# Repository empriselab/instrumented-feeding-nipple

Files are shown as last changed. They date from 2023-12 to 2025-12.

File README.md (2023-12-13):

# Instrumented Feeding Nipple

## CAD Files
All CAD files were printed using 5% rectilinear infill and no supports. A tutorial on how to construct the nipple can be found here: https://www.youtube.com/watch?v=TO4Haf6ZgnU

## Calibration 
The following must be run within `feeding_nipple_ws` which is the workspace to run the ATI Net F/T sensor.

### Step 1: Upload the Arduino code
Upload the `FeedingNippleArduino.ino` to your Arduino. Calibrate the upper and lower bounds of the analogRead and its corresponding voltages to ensure accurate readings. Be sure the readings are printing properly on the serial monitor. Ensure the serial monitor is closed throughout the duration of data collection.

### Step 2: Start ATI NET F/T sensor
Turn on the ATI NET F/T sensor. Open your terminal. Remember to run `source devel/setup.bash` everytime you open a new window in the root of your workspace to source it.

To initialize the core, type `roscore`.

In a new window, launch the sensor topic by typing `roslaunch netft_rdt_driver ft_sensor.launch ip_address:=192.168.1.6 bias:=True rate:=1000`.

To ensure the topic has been properly launched, type the command `rostopic echo /ft_sensor/netft_data`. This will allow you to monitor the readings from the F/T sensor in real time.

Calibrate the F/T sensor by holding it in the air and typing the command `rosservice call /ft_sensor/bias_cmd "cmd: 'bias'"`.

### Step 3: Begin collecting data
Run the bash script `callibration.sh` in the feeding_nipple_ws to begin collecting data from the ATI NET F/T sensor.

### Step 4: Convert Rosbag into CSV file
Place the `extract_forque.py` script in the same folder as your rosbag files. Run the `extract_forque.py` script. This converts the rosbag into a CSV in its own individual folder.

### Step 5: Combine the Force and Voltage Readings using CurveFit.py
Run this script with two CSVs files as the input - the voltage readings from the Arduino and the rosbag force readings. This script will combine the two csv files and calculate a calibration function in the form y = ae^(bx).

## Post-Calibration 
After finding the calibration function, input the a and b parameters into `TranslateV2F.py`. Whenever performing future tests or in field tests, have `FeedingNippleArduino.ino` running on the Arduino before running `TranslateV2F.py`.

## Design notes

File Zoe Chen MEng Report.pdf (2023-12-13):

# DESCRIBING CHANGES IN SUCKLE BEHAVIOR VIA TACTILE FEEDING NIPPLE BETWEEN HEALTHY & SICK DAIRY BREED CALVES

A Design Project Report

Presented to the School of Electrical and Computer Engineering of Cornell University

in Partial Fulfillment of the Requirements for the Degree of

Master of Engineering, Electrical and Computer Engineering

Submitted by

Zoe Mallorie Chen

MEng Field Advisor: Tapomayukh Bhattacharjee

MEng Outside Advisor: Taika von Königslöw

Degree Date: January 2024

INSTRUMENTED CALF FEEDING NIPPLE

# Abstract

Master of Engineering Program

School of Electrical and Computer Engineering

Cornell University

Design Project Report

Project Title:
Describing Changes in Suckle Behavior Via Tactile Feeding Nipple Between Healthy & Sick Dairy Breed Calves

Author:
Zoe Mallorie Chen

Abstract:
Treating young calves promptly is challenging for caregivers because the diagnosis process is labor intensive and potentially a biohazard when multiple calves are involved. Previous studies have found that sickly calves exhibit weak suckling behavior – however, exact quantifiable differences in the bite force have yet to be defined. The goal is to create a robust instrumented feeding nipple that characterizes suckling behavior in the two groups. In the current iteration, we created a system that accurately measures bite forces of up to 50N and conducted preliminary field tests using portable milk feeders. We hope to integrate it into the commercial automated milk feeders to provide a quantified indicator of illness for early treatment and to improve clinical outcomes.

1

## 1 Executive Summary

Weaker biting forces correlate to diseased calves, especially those under six months suffering from diarrhea. The planned final product is a sensor that fits within current calf feeding systems to record the bite force of calves during the suckling process – in hopes of providing another illness indicator that is safer and more convenient for caregivers. The product must be rugged enough to withstand variations in temperature, exposure to liquids, and over fourteen thousand bites over its lifetime – all while maintaining a soft exterior that is comfortable for the calves to chew on.

The current iteration of the sensor is modeled after the feeding nipples attached to portable calf milk feeding bottles. Two force resistive sensors (FSRs) are encapsulated within two silicon layers and wired to a Wheatstone bridge. The output voltage is converted to a force via a calibration function in the form of an exponential growth function. All voltage-to-force translations are done on an Arduino Nano 33 IOT in real-time. The total cost of the sensor is $20.36, excluding the cost of the microcontroller.

We have validated that the design’s calibration function adequately fits the industry standard. Comparisons between the developed sensor and the ground truth force have shown that the sensor accurately and precisely measures the true force up to 50N, with an error of ±3.09N.

Preliminary field testing found that healthy bites (N=160) had an average force of 14.97N with a standard deviation of 4.30N, while weak bites (N=221) had an average force of 4.55N with a standard deviation of 2.35N.

2

## 2 Background

To assess a calf’s condition during health checks, caregivers typically look for subtle visual cues (e.g. depression, alertness) [3]. Reliance on these cues remains an issue because cows are a prey species and tend to hide their sickness as a protection mechanism against predators. Once signs of sickness present themselves, such as diarrhea and dehydration, the calf may have already sustained damage to its internal organs – driving the need for systems that help caregivers predict or detect illness in calves earlier than currently possible [3].

A few quantitative measures exist to help with the earlier identification of sick calves, such as elevated rectal temperatures. However, these methods provide no continuous monitoring options, are time-consuming, or require direct contact with feces– which may become a biohazard because of zoonotic pathogens [5].

Previous studies have shown that sickly calves generally have weaker suckling behavior than their healthy counterparts, but quantifiable differences in the bite forces between these two groups have yet to be defined [3]. The goal of this project is to create a sensor that defines the bite force differences between healthy and sickly calves, with the hopes of developing a general tactile sensor fit for rugged conditions.

3

## 3 Design Requirements

The sensor developed for this project must be embedded within feeding nipples used on portable milk feeding bottles. These feeding nipples are typically replaced once every 2 weeks, subjected to a wide range of temperatures, and exposed to liquids.

Given these standards, we aim to embed a sensor that measures bite force within a feeding nipple, ensuring that the final product is capable of:

- Accurately and precisely measuring bite forces of up to 50N
- Withstanding over fourteen-thousand chews without signal degradation
- Working when external liquids are introduced
- Maintaining consistent signal readings during temperature fluctuations
- Being inexpensive to facilitate frequent replacements

4

## 4 Implementation

### 4.1 Force Sensors

Force sensing resistors (FSRs) were chosen for this iteration among capacitance and magnetic sensors because of their durability, circuit simplicity, noise resistance, force repeatability, and lost cost of production. These sensors must also be flexible enough for the calves to chew on and must be able to differentiate between forces of at least up to 11N, as estimated by our calculation from the typical bite pressure and surface area of a calf’s molars:

236 kPa × 0. 0075 m × 0. 006 m = 10. 62N

Given these requirements, we chose the Interlink Electronics FSR UX 406 series. Both long and short versions of this FSR were tested. Although the long version had more structural integrity, the final design opted for the short version because of our size constraints [2].

### 4.2 Mechanical Assembly

### 4.2.1 Silicon Mixture

Various mixtures of silicon were tested to create a product most similar in texture and stiffness to the current silicon rubber nipples on portable milk feeding containers. The final product utilizes Smooth-On PMC™-770, a mixture that has a shore hardness of 70A or similar to the sole of a shoe.

Thirty grams of Part A and fifteen grams of Part B of PMC™-770 are thoroughly mixed before being poured into 3 custom 3D printed molds. The result from the custom molds are as follows:

- A cylindrical inner layer that protects the sensors from milk within the feeder.
- A cylindrical outer layer that protects the sensor from degradation from the environment and calf chewing.
- A circular ring adhered to the outer and inner layer to keep the nipple attached to the bottle.

5

All molds are left to cure for at least sixteen hours at room temperature before being demolded.

### 4.2.2 FSR Wire Extensions

To date, the FSR UX 406 from Interlink Electronics only offers solder tab connections. Two wires are soldered onto those tabs – with careful consideration towards the heat of the soldering iron and stress applied to the joint, as these tabs are very fragile. We have found that wrapping the joint in electrical tape and setting the temperature of iron to just enough for the solder to melt significantly reduces the chance of tab breakages.

### 4.2.3 Components Layering

Two types of glue are used to ensure the FSRs stay in their designated areas during the setting and drying process. RapidFuse® All-Purpose Adhesive has a quick set time of thirty seconds and is initially applied to ensure the FSRs are centered throughout the entire glue curing process. E6000, an industrial strength adhesive, is then applied to increase the bond strength between the FSRs and the silicon rubber.

Four FSRs, two on each hemisphere, are adhered to the cylindrical inner layer by applying small amounts of RapidFuse® All-Purpose Adhesive to the back of the FSRs. The FSRs are held in place until the glue sets before E6000 is then applied to the back of the FSRs. A custom 3D print has been created to hold the FSRs in a circular shape during the curing process. After the E6000 is cured, the FSRs and the inner cylindrical layer is encapsulated within the outer cylindrical layer and the two layers are adhered to the silicon circular ring using the E6000. The wires from the FSRs are routed through the ring or above the ring depending on whether a milk or no milk version of the nipple is being created.

For the milk version of the nipple, a custom 3D printed box with a lid has been created to house the circuitry. The box is attached to the box via velcro. If opting for a no milk version of the nipple, a panel the size of the breadboard is cut out of the milk container and attached back to the container using a plastic hinge to create a panel for easy access to the circuitry. The breadboard can be attached to the panel via velcro or other adhesives.

6

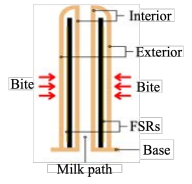
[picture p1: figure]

Figure 1. Cross section of a feeding nipple with only two FSRs.

Figure 2. Non-milk version of the manufacturing sample, with circuitry attached to a panel created by cutting out the portable milk feeder.

7

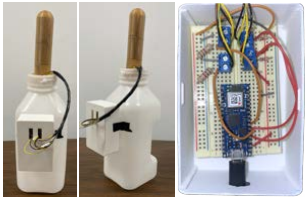
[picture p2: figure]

Figure 3. Milk version of the manufacturing sample, with circuitry (left) attached to the side of the portable feeder (right, middle).

### 4.3 Circuitry

The original circuitry design featured four FSRs, each a part of a two resistor voltage divider circuit. Initially testing found that this circuitry provided a narrow voltage output range of 0 to 2000 mV to forces between 0 to 50N – making it difficult to map a voltage to a force with certainty.

The final circuitry design instead features a pair of FSRs connected in one wheatstone bridge – for a total of two wheatstone bridges in this iteration of the project. Pairs of the wheatstone bridge are defined as FSRs that are directly across from each other on the nipple. To determine the values of R2 and R3, the following equation was used:

Vout = Vdd( | ,

R3
R

FSR1+R3 − R FSR2 R2 + R FSR2 )

such that the output voltage is 0 when no force is applied. The working principle is that when a calf bites on the FSRs, the resistances of those FSRs simultaneously decreases, causing the positive and negative terminals of the output voltage to increase and decrease respectively. This resulted in a new output voltage range of -3300mV to 1000mV, doubling the voltage range that we can map onto a bite force.

8

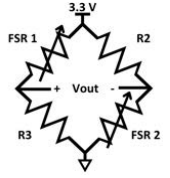
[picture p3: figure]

Figure 4. Schematic for one wheatstone bridge configuration.

### 4.4 Calibration

A drill press vise with a stationary base and the ATI Net F/T sensor were used to map the output voltages from the wheatstone bridge to a bite force. The Net F/T sensor is an external device we used to define the industry standards for force measuring instruments – which will now be referred to as the ground-truth force. The manufactured product and the Net F/T sensor were placed between the stationary and moving jaw.

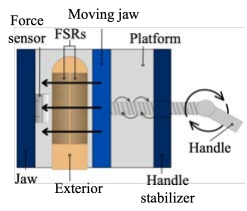
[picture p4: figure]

Figure 5. Sketch of the calibration setup using a bench drill press vise and ATI Net F/T sensor.

9

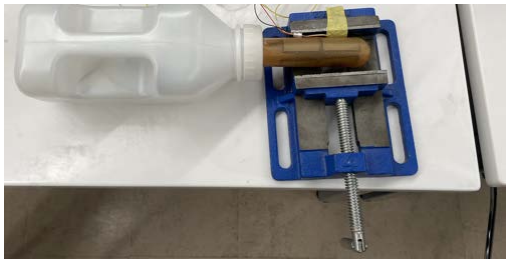
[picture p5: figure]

Figure 6. Manufactured sample placed inside drill press with force sensor, which is attached using yellow tape.

Thirty thousand samples from both the Net F/T sensor and the output voltage were recorded before being averaged by ground-truth force. The trend between increases in the output voltage and the ground-truth force most closely followed an exponential growth form with a standard deviation of ±3.09N, which was used as the mathematical model to relate the ground-truth force and the output voltage.

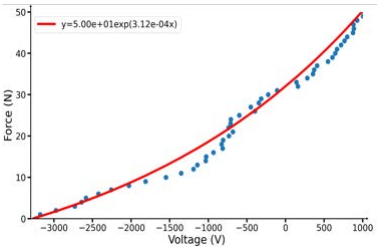
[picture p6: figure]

Figure 7. Voltage-force relation when force is applied. Line of best fit is shown in red for one specific sample.

10

## 5 Validation

Comparisons between the force estimates from the proposed product and the ground-truth force were conducted, using the drill press vise to mimic a chewing motion. Our trials found that our sensor’s estimates were within one standard deviation of the ground-truth force sensors from 0 to 50 N.

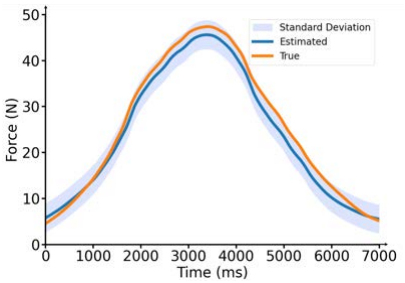
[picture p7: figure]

Figure 8. Estimated force (dark blue) with standard deviation (light blue) and ground truth force from external sensor (orange).

Trials were also conducted with live calves to determine whether the proposed product was capable of sensing differences between weak and healthy bite forces during suckling behaviors. During these experiments, weak bites were defined as non-suckling chewing behavior, such as play. Our trials found that healthy bites (N=160) had an average force of 14.97N with a standard deviation of 4.30N, while weak bites (N=221) had an average force of 4.55N with a standard deviation of 2.35N. The FSRs during these trials showed no signs of signal degradation and no major deformations were found on the silicon nipples after chewing.

11

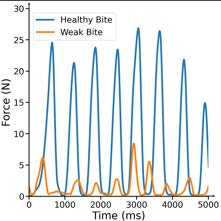
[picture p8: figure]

Figure 9. Estimated force from calves with healthy and weak bites.

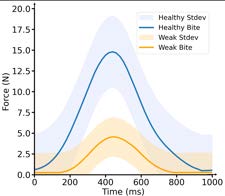
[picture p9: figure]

Figure 10. Average healthy (N = 160) and weak (N = 221) bites force from field trials.

12

## 6 Conclusion

Our testing and preliminary tests revealed some flaws with the current iteration of the proposed product. The current iteration with four FSRs total has a diameter and length that is too wide to comfortably fit within the mouth of calves – which caused the calves to engage in play behavior instead of suckling behavior. A smaller and narrower sensor with only two FSRs total should be developed to consistently encourage calf suckling behavior.
In addition, the generalized mathematical function | typically y = ae

bx
does not translate well from sample to sample due to inconsistencies in the manufacturing process, and thus requires the parameters and to be calibrated a b for each specific sensor.
This iteration of the sensor requires a microcontroller with a wired connection to communicate with the serial monitor and allow a Python program to write the data into a csv file. Future iterations of this sensor should be self contained to make the sensor truly portable and for caregiver ease.
Finally, the total cost of the sensor is $20.36, excluding the cost of the Arduino 33 IOT. Considering that typical cow feeding nipples range from $1 to $4 and that these nipples are replaced frequently, a less expensive sensor should be developed. The largest factor in our sensor cost were the four FSRs, which totaled $19.96. Even if a sensor were developed with only two FSRs to more comfortably fit within the calf’s mouth, the total cost would still exceed our requirements. One possible solution is to create flex sensors ourselves, which are considerably cheaper than those on the market [1][4]. Further testing is required to characterize these homemade flex sensors and how they compare to commercially available FSRs.

13

## 7 Appendix

A video tutorial of the process described below can be found here. (https://youtu.be/TO4Haf6ZgnU)

### 7.1 Nipple Construction

### 7.1.1 Silicon Molding

The custom molds are 3D printed with a 5% infill and PLA. A version of the molds for two FSRs have been provided. Line your surface with aluminum foil. Measure 15g and 7.5g of Part A and Part B of Smooth-On PMC™-770 using a scale and pour the mixture into a disposable cup. Mix together thoroughly for 3 minutes using a wooden tongue depressor. Spray a thin coating of Universal™ Mold Release, or any mold release, onto all surfaces of the outer layer, inner layer, and ring molds. Make sure the coat is evenly distributed using a paint brush. Pour your silicon mixture into the base molds and place the shapers in their respective base molds. The shapers should snap into place using the prongs from the base molds. Allow to cure for at least 16 hours before demolding.

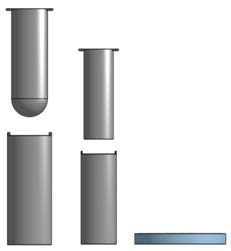
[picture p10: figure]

Figure 11. CAD models for the custom molds of the nipple for only two FSRs. Bottom: the base mold for the outer layer (left), the inner layer (middle), and the

14 ring. Top: the shaper of the outer mold (left) and the shaper for the inner mold (middle).

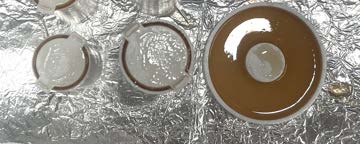
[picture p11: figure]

Figure 12. Top view of the inner layer (left), outer layer (middle), and ring (right) molds with silicone poured into them.

Figure 13. Side view of all molds, closeup of the outer layer mold (middle), and closeup of the ring mold (right).

Sometimes, the silicon expands, making it difficult to remove from the mold by sliding the shaper out. In this case, use the backside of a hammer to break a line down the center of molds.

15

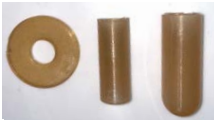
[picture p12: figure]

Figure 14. Silicon parts demolded.

### 7.1.2 FSR Wire Extensions

Solder two 24 AWG wires onto each lead of each FSRs. Be sure to heat the soldering iron to the minimum temperature required to melt the solder, as excessive heat may damage the leads of the FSR and cause them to melt off. To minimize breakage at these points, wrap the leads with tape.

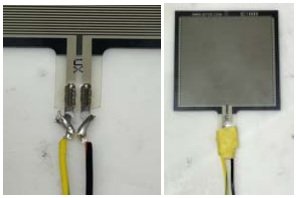
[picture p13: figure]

Figure 15. FSR soldered with 24 AWG wires (left) and wrapped with tape (right).

### 7.1.3 Component Layering

Once all the FSRs are soldered, apply a small amount of RapidFuse® All-Purpose Adhesive to the back of the FSRs and adhere them to the silicon inner layer. Place inside the custom 3D printed holder and wait for 30 minutes, or until the glue cures. Once that glue cures, add E6000 adhesive to the back of the FSRs. Allow to cure for 24 hours.

16

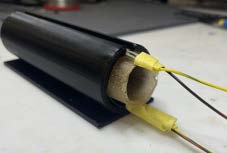
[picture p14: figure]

Figure 16. FSRs glue and placed into a custom 3D printed holder.

After the E6000 cures, encapsulate the inner layer with the outer layer and glue both to the ring using the E6000. Place upright and allow to dry for 24 hours. This nipple should screw onto the portable milk feeder.

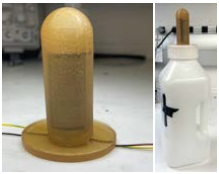
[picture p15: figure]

Figure 17. Constructed nipple (left) and screwed into feeder (right).

### 7.2 Calibration

Place the sensor within the two jaws of a drill press vise with a stationary base. Attach the ATI Net F/T sensor to the stationary jaw of the drill press vise such that it directly aligns with the center of one of the FSRs (Figure 6). When calibrating, be sure that voltage outputs from all forces ranging from 0 to 50N, in increments of 5N or less, are being recorded. Code to start the FT sensor, the Arduino, and to combine the readings between the two devices to generate a mathematical model.

17

## References

[1] Ardi Wiranata et al., “A DIY Fabrication Approach of Stretchable Sensors Using Carbon Nano Tube Powder for Wearable Device,” Frontiers in Robotics and AI, vol. 8, Nov. 2021, doi: https://doi.org/10.3389/frobt.2021.773056.
[2] “FSR UX 406 Short,” Interlink Electronics Shop. https://buyinterlinkelectronics.com/products/fsr-ux-406-short
[3] G. L. Lowe, M. A. Sutherland, J. R. Waas, A. L. Schaefer, N. R. Cox, and M. Stewart, “Physiological and behavioral responses as indicators for early disease detection in dairy calves,” Journal of Dairy Science, vol. 102, no. 6, pp. 5389–5402, Jun. 2019, doi: https://doi.org/10.3168/jds.2018-15701.
[4] K. Elgeneidy, G. Neumann, M. Jackson, and N. Lohse, “Directly Printable Flexible Strain Sensors for Bending and Contact Feedback of Soft Actuators,” Frontiers in Robotics and AI, vol. 5, Feb. 2018, doi: https://doi.org/10.3389/frobt.2018.00002.
[5] Mikolt Bakony, Levente Kovács, Luca Fruzsina Kézér, and V. Jurkovich, “The use of body surface temperatures in assessing thermal status of hutch-reared dairy calves in shaded and unshaded conditions,” Frontiers in Veterinary Science, vol. 10, Jul. 2023, doi: https://doi.org/10.3389/fvets.2023.1162708.

18

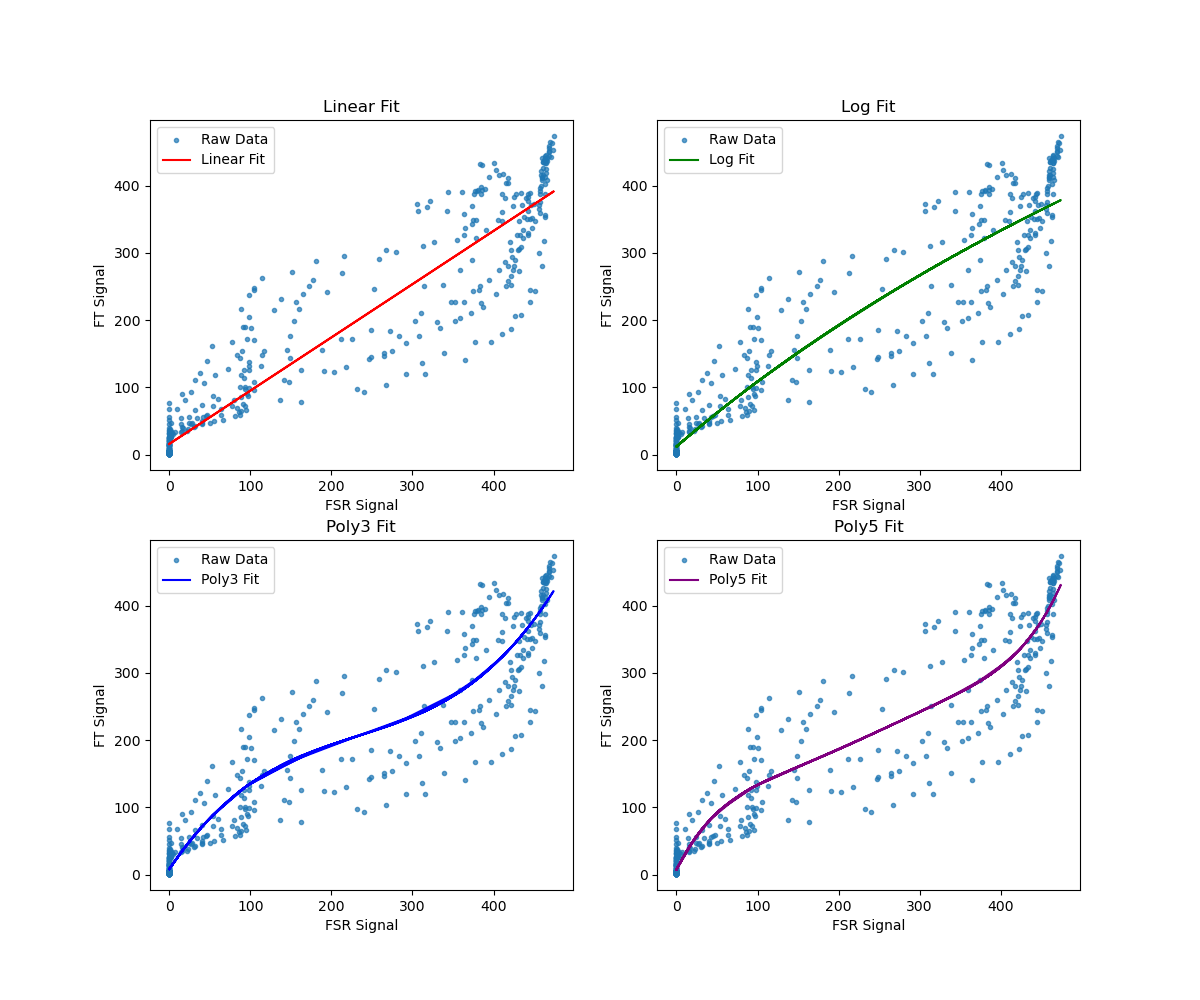
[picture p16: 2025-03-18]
scripts/diff_fit_models.png

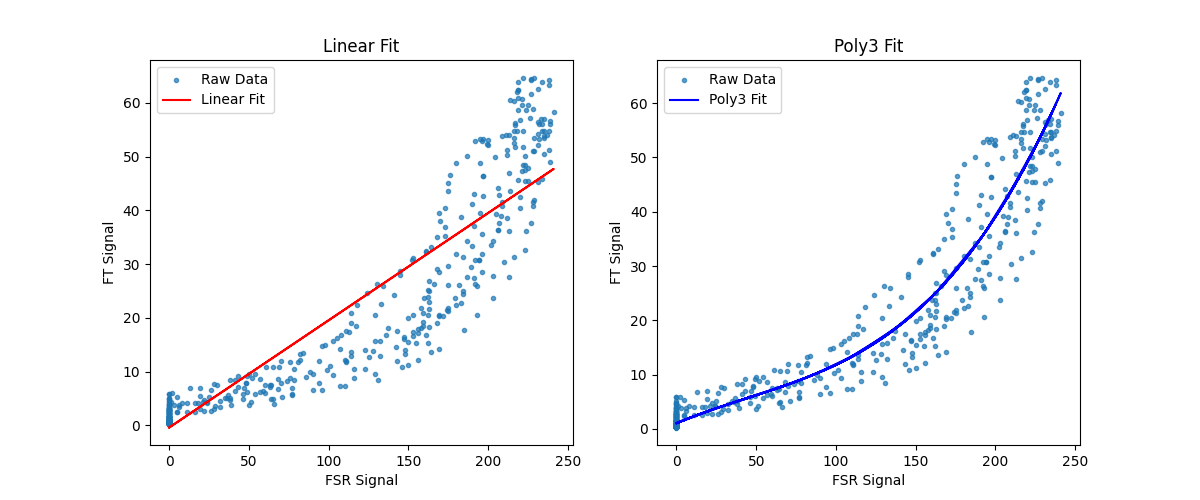
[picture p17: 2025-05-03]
scripts/flat_iter_1_diff_fit_models.png

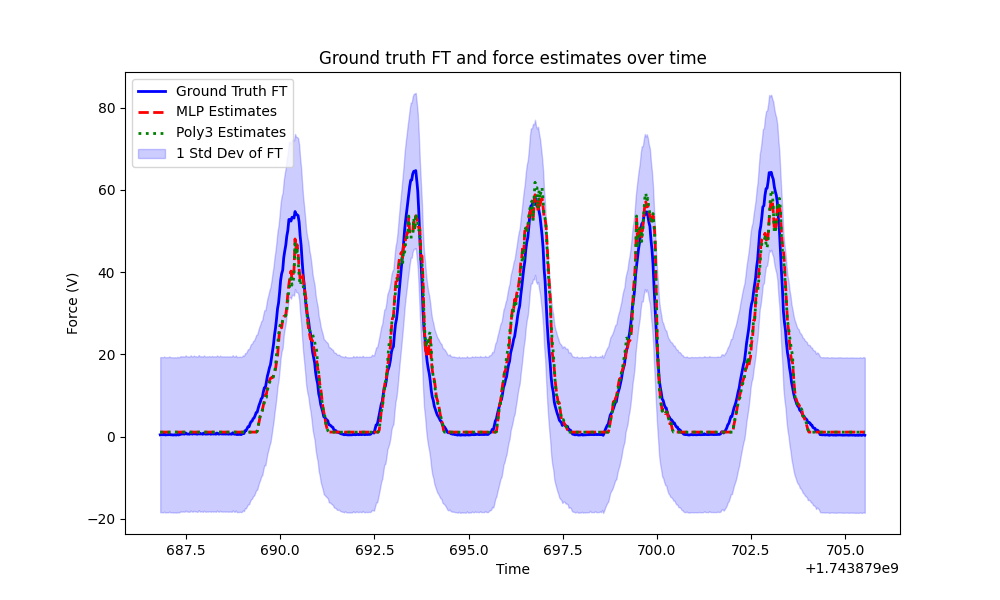
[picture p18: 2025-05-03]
scripts/flat_iter_1_compare_time_force.png

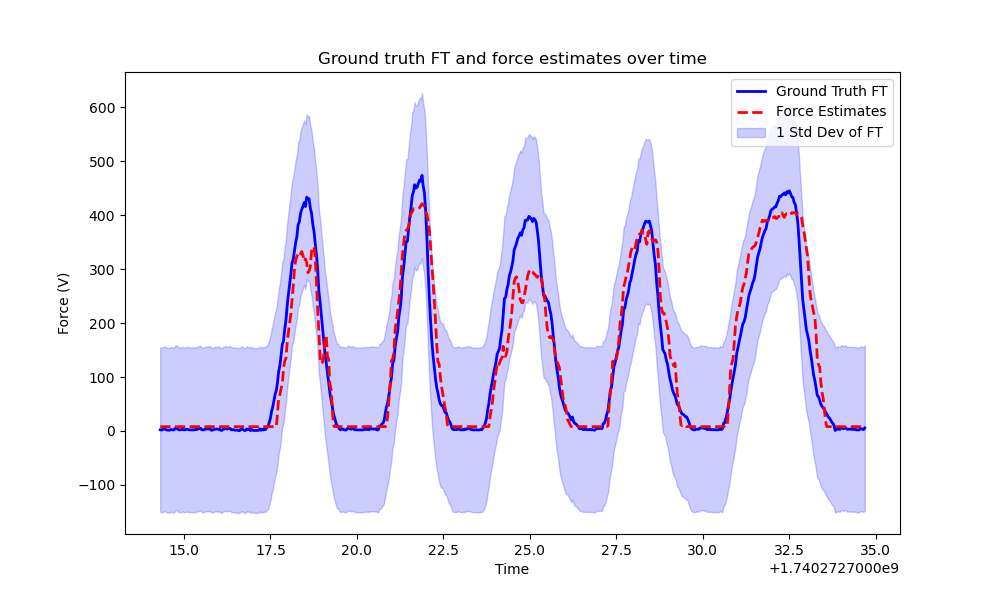
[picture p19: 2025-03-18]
scripts/compare_time_force.png

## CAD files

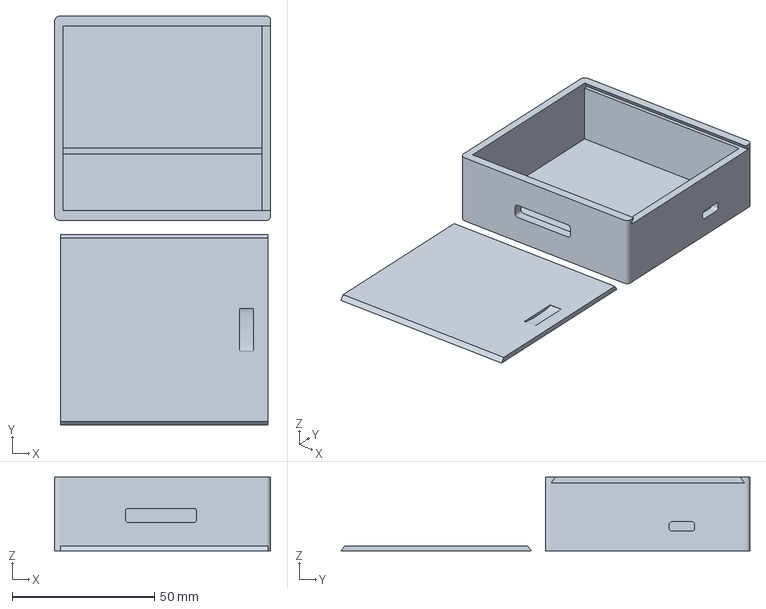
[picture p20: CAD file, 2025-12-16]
CAD/Instrumented Feeding Bottle Box v2.3mf
76.0 x 143.8 x 26.0 mm

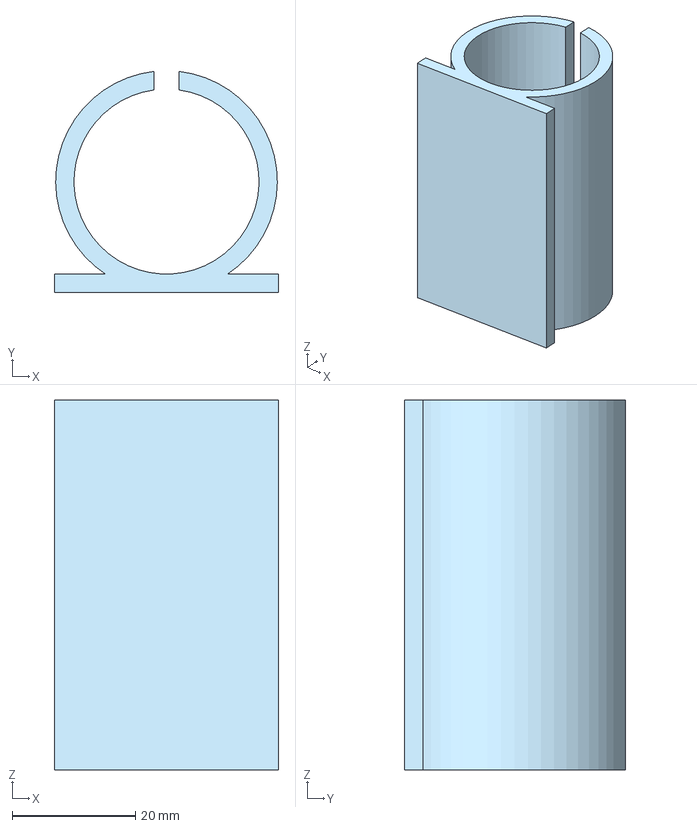
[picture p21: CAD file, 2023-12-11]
CAD/DryingRack.step
36.3 x 35.9 x 60.0 mm

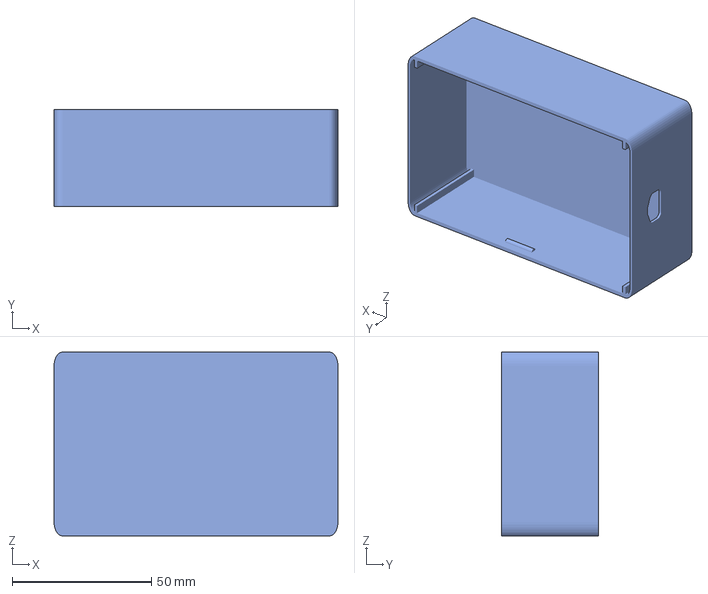
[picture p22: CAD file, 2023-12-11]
CAD/BreadboardBoxCase.step
102.0 x 35.0 x 66.0 mm

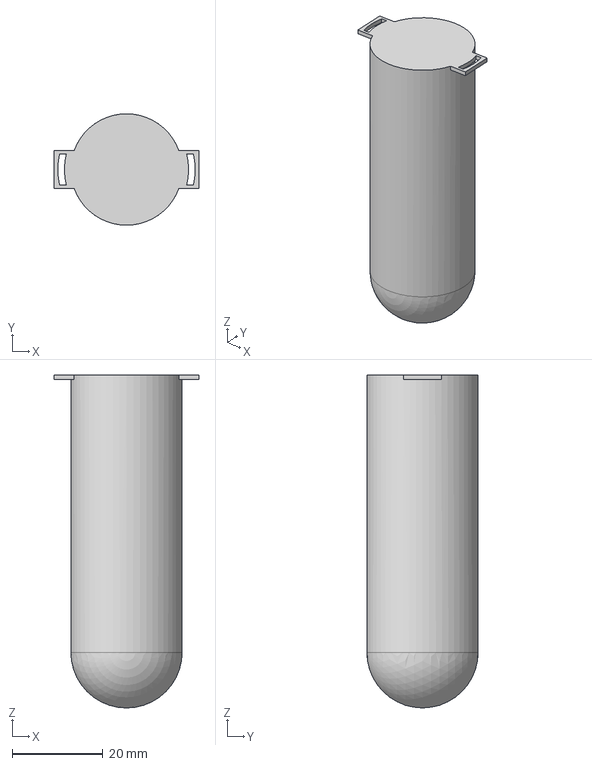
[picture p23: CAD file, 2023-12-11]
CAD/Outer Mold - Shaper.step
31.8 x 24.5 x 73.2 mm

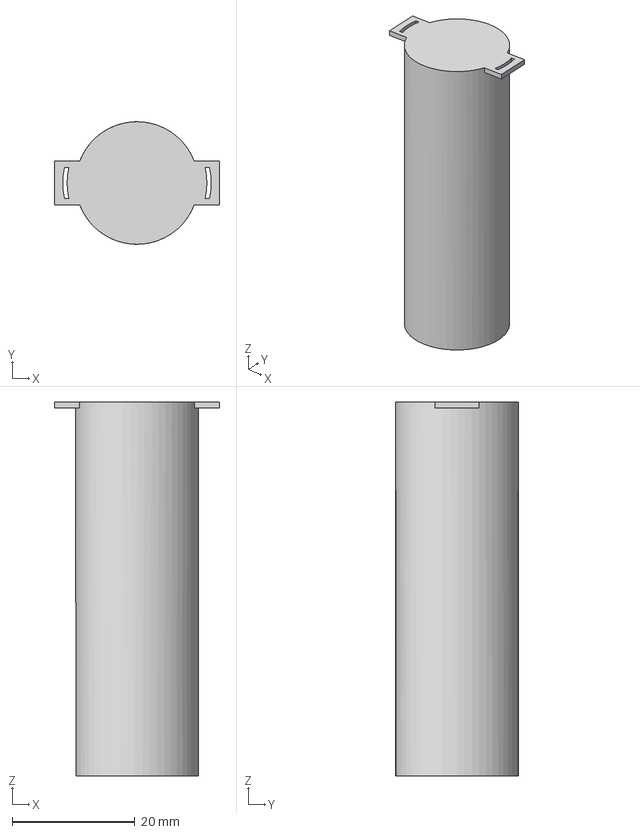
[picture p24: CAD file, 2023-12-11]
CAD/Inner Mold - Shaper.step
26.9 x 20.0 x 61.0 mm

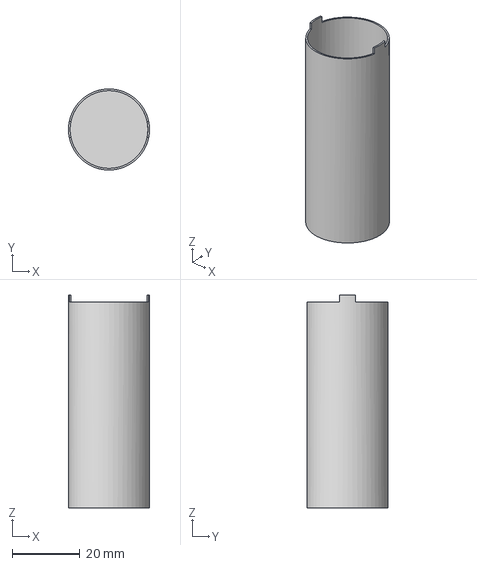
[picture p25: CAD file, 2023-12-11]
CAD/Inner Mold - Outer Container.step
24.0 x 24.0 x 63.0 mm

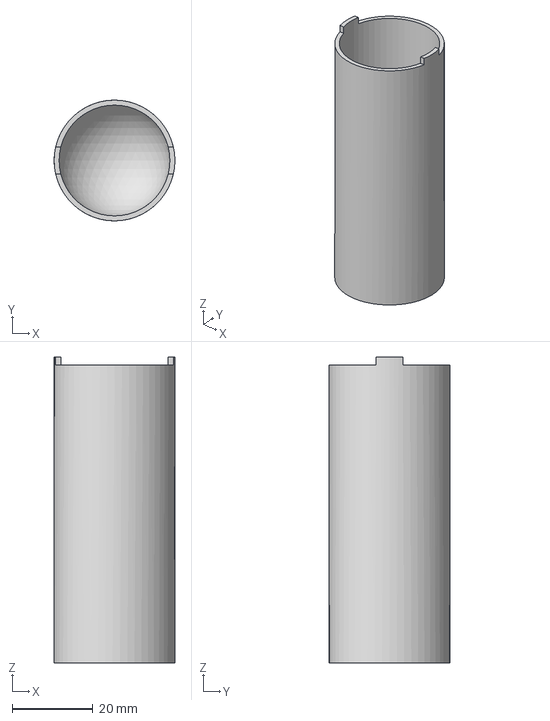
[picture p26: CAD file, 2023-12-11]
CAD/Outer Mold - Container.step
30.0 x 30.0 x 76.0 mm

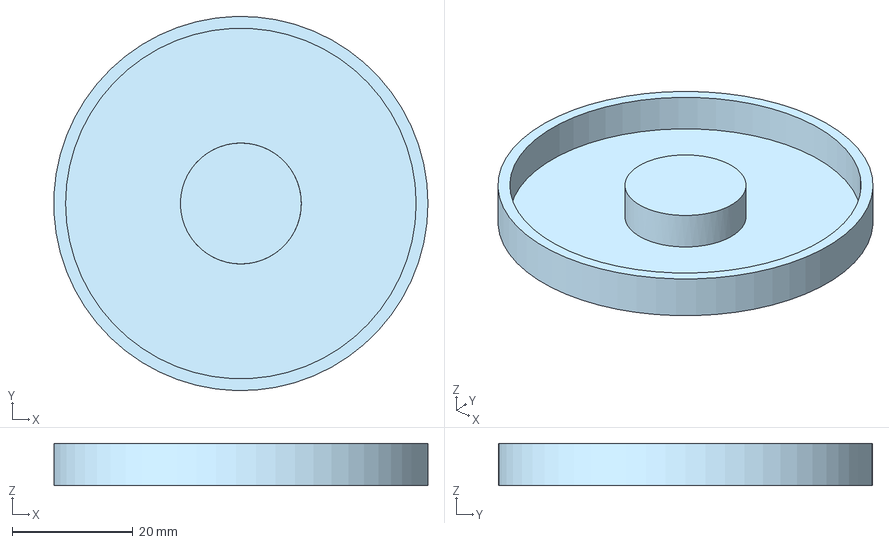
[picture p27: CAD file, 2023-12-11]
CAD/Ring.step
61.9 x 61.9 x 7.00 mm

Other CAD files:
CAD/BreadboardBoxLid.step

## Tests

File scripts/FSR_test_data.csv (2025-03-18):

Timestamp | FSR 1 (mV) | FSR 2 (mV) | FSR 3 (mV) | FSR 4 (mV) | FSR 5 (mV) | FSR 6 (mV) | FSR 7 (mV) | FSR 8 (mV)
1740272712.2905614 | 4 | 662 | 491 | 767 | 453 | 625 | 660 | 823
1740272712.3242462 | 12 | 597 | 482 | 768 | 453 | 626 | 659 | 822
1740272712.3612447 | 10 | 596 | 482 | 768 | 453 | 626 | 659 | 821
1740272712.393989 | 11 | 599 | 483 | 769 | 453 | 626 | 659 | 820
1740272712.4268672 | 10 | 599 | 482 | 768 | 453 | 626 | 659 | 820
1740272712.4635546 | 11 | 597 | 481 | 768 | 453 | 626 | 659 | 820
1740272712.4957674 | 11 | 598 | 482 | 768 | 453 | 625 | 659 | 820
1740272712.5285187 | 11 | 599 | 482 | 768 | 453 | 626 | 659 | 820
1740272712.5651255 | 10 | 597 | 482 | 768 | 454 | 625 | 659 | 820
1740272712.5985641 | 10 | 597 | 482 | 768 | 453 | 626 | 659 | 820
1740272712.6349564 | 11 | 598 | 482 | 768 | 453 | 625 | 659 | 820
1740272712.6677067 | 11 | 599 | 481 | 765 | 454 | 624 | 659 | 820
1740272712.7013493 | 11 | 598 | 483 | 768 | 453 | 626 | 659 | 820
1740272712.7376175 | 11 | 598 | 483 | 768 | 453 | 626 | 659 | 820
1740272712.7703927 | 11 | 599 | 482 | 768 | 453 | 625 | 659 | 820
1740272712.8035338 | 11 | 597 | 482 | 767 | 454 | 626 | 659 | 820
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

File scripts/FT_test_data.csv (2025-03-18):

ft_time | ft
1740272714.3016016 | -0.19743083302020992
1740272714.302462 | -0.17948224453826603
1740272714.3034663 | -0.20844243196550447
1740272714.3044705 | -0.2187319158313526
1740272714.3054733 | -0.17101106203861202
1740272714.3064775 | -0.217084160826473
1740272714.307481 | -0.5791213030014477
1740272714.3084843 | -0.38585826885157515
1740272714.3094873 | -0.44596411802688196
1740272714.3104913 | -0.17453741164178502
1740272714.3114953 | -0.19585322173713085
1740272714.3124988 | -0.2281481302720972
1740272714.3135018 | -0.37197490208788775
1740272714.3145046 | -0.32694662341858444
1740272714.315509 | -0.2478086346029407
1740272714.3165133 | -0.29067436110165173
1740272714.3175168 | -0.1737111814015836
1740272714.3185203 | -0.15331018309862463
1740272714.3195236 | -0.16424768230149844
1740272714.3205295 | -0.16442833284921973
1740272714.3215325 | -0.14062355664913956
1740272714.3225367 | -0.1457234366806307
1740272714.323545 | -0.1570450338300895
1740272714.324543 | -0.5178950170235416
1740272714.325546 | -0.3582621785311061
1740272714.3265502 | -0.18045592132832347
1740272714.3275535 | -0.1525393731159726
1740272714.3285575 | -0.1684101787797096
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

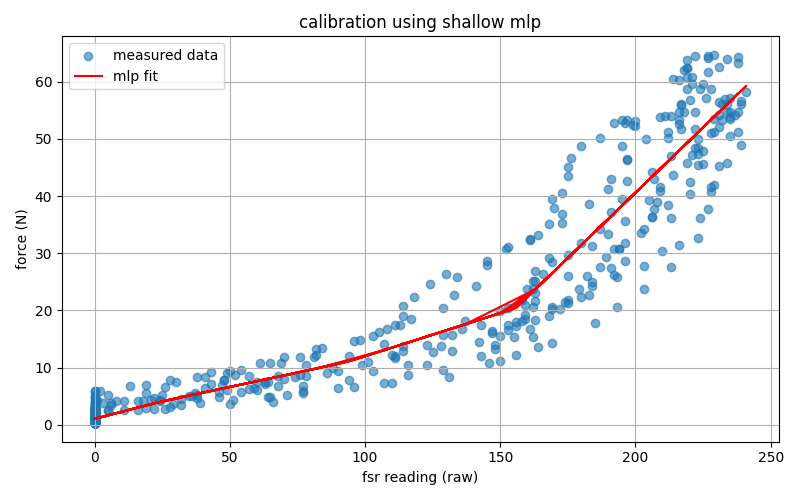
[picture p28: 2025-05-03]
scripts/flat_mlp_calibrated.png

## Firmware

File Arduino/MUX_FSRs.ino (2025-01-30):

// Pin declarations for the sensors and MUX control
int pos_Vout = A0; // Assume the multiplexer output is connected to A0
int neg_Vout = A1;
const int muxS0 = 2; // Multiplexer control pins
const int muxS1 = 3;
const int muxS2 = 4;
// const int muxS3 = 5;

// Number of FSRs and MUX channels
const int numFSRs = 16;

// Array to store offsets for zeroing out readings
float offset[numFSRs] = {0};

// Number of samples to collect for calibration and averaging
const int numSamples = 10;

void setup() {
  Serial.begin(9600);  // Initialize the serial communication

  // Set MUX control pins as output
  pinMode(muxS0, OUTPUT);
  pinMode(muxS1, OUTPUT);
  pinMode(muxS2, OUTPUT);
  pinMode(muxS3, OUTPUT);

  // Calibrate offsets
  Serial.println("Calibrating offsets...");
  calibrateOffsets();
  Serial.println("Calibration complete!");
}

void loop() {
  for (int fsrIndex = 0; fsrIndex < numFSRs; fsrIndex++) {
    // Set MUX to the correct channel for the current FSR
    setMuxChannel(fsrIndex);
    delay(5); // Allow time for MUX to settle

    // Initialize variables for averaging
    long sumForceReading = 0;

    // Read and sum samples
    for (int i = 0; i < numSamples; i++) {
      float sensorUpper = analogRead(pos_Vout);
      float sensorLower = analogRead(neg_Vout);
      sumForceReading += (sensorUpper - sensorLower);
    }

    // Calculate the average and apply offset
    float average = (float)sumForceReading / numSamples - offset[fsrIndex];

    // Print the reading for the current FSR
    Serial.print("FSR ");
    Serial.print(fsrIndex);
    Serial.print(": ");
    Serial.println(average);
  }

  delay(100); // Adjust delay as needed for reading frequency
}

// Function to calibrate offsets
void calibrateOffsets() {
  for (int fsrIndex = 0; fsrIndex < numFSRs; fsrIndex++) {
    // Set MUX to the correct channel for the current FSR
    setMuxChannel(fsrIndex);
    delay(5); // Allow time for MUX to settle

    // Initialize variables for averaging
    long sumForceReading = 0;

    // Read and sum samples
    for (int i = 0; i < numSamples; i++) {
      float sensorUpper = analogRead(pos_Vout);
      float sensorLower = analogRead(neg_Vout);
      sumForceReading += (sensorUpper - sensorLower);
    }

    // Calculate the average and store as offset
    offset[fsrIndex] = (float)sumForceReading / numSamples;

    Serial.print("Offset for FSR ");
    Serial.print(fsrIndex);
    Serial.print(": ");
    Serial.println(offset[fsrIndex]);
  }
}

// Function to set the MUX channel
void setMuxChannel(int channel) {
  digitalWrite(muxS0, channel & 0x01);
  digitalWrite(muxS1, (channel >> 1) & 0x01);
  digitalWrite(muxS2, (channel >> 2) & 0x01);
  digitalWrite(muxS3, (channel >> 3) & 0x01);
}

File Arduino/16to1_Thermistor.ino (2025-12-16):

#include <math.h>

// --- MUX FSR SETUP ---
const int muxSigPin = A0;       // MUX signal pin (connected to FSRs)
const int s0Pin = 2;            // MUX control pins
const int s1Pin = 3;
const int s2Pin = 4;
const int s3Pin = 5;

const int numFSRChannels = 12;  // Number of FSRs
int fsrReadings[numFSRChannels];

// --- Thermistor SETUP ---
#define THERMISTORPIN A1  
#define THERMISTORNOMINAL 10000      
#define TEMPERATURENOMINAL 25   
#define NUMSAMPLES 5
#define BCOEFFICIENT 3950
#define SERIESRESISTOR 10000    

int samples[NUMSAMPLES];

void setup() {
  Serial.begin(9600);

  // MUX control pins
  pinMode(s0Pin, OUTPUT);
  pinMode(s1Pin, OUTPUT);
  pinMode(s2Pin, OUTPUT);
  pinMode(s3Pin, OUTPUT);

  // Initialize MUX control lines
  digitalWrite(s0Pin, LOW);
  digitalWrite(s1Pin, LOW);
  digitalWrite(s2Pin, LOW);
  digitalWrite(s3Pin, LOW);

  analogReference(AR_EXTERNAL);
}

void loop() {
  // --- Read FSRs ---
  for (int channel = 0; channel < numFSRChannels; channel++) {
    selectMuxChannel(channel);
    fsrReadings[channel] = analogRead(muxSigPin);
  }

  // --- Read Thermistor ---
  float average = 0;
  for (int i = 0; i < NUMSAMPLES; i++) {
    samples[i] = analogRead(THERMISTORPIN);
    delay(2);
  }
  for (int i = 0; i < NUMSAMPLES; i++) {
    average += samples[i];
  }
  average /= NUMSAMPLES;

  // Convert ADC reading to resistance
  average = 1023.0 / average - 1.0;
  average = SERIESRESISTOR / average;

  float steinhart;
  steinhart = average / THERMISTORNOMINAL;
  steinhart = log(steinhart);
  steinhart /= BCOEFFICIENT;
  steinhart += 1.0 / (TEMPERATURENOMINAL + 273.15);
  steinhart = 1.0 / steinhart;
  steinhart -= 273.15;

  // --- Print Data in One Line: FSR1 FSR2 ... TempC ---
  for (int i = 0; i < numFSRChannels; i++) {
    Serial.print(fsrReadings[i]);
    Serial.print(" ");
  }
  Serial.println(steinhart);  // temperature in °C
}

// --- Select MUX Channel ---
void selectMuxChannel(int channel) {
  digitalWrite(s0Pin, (channel & 0x01));
  digitalWrite(s1Pin, (channel & 0x02) >> 1);
  digitalWrite(s2Pin, (channel & 0x04) >> 2);
  digitalWrite(s3Pin, (channel & 0x08) >> 3);
}

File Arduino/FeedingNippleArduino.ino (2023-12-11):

//Sketch uploaded to Arduino Nano 33 IOT to read voltages from the positive and negative terminals of the output voltage. Before starting, be sure to 
//calibrate the bounds for the AnalogRead and their respective voltages (lines 21-35) using a multimeter and lines 45-47. The lower bounds are defined as 
//when no force is applied to the sensors and the upper bounds are defined as when the force applied results in a voltage of ~3.3V.



//pin declarations for the sensors
int pos_Vout = 14;
int neg_Vout = 15;
int c = 0;

// Number of samples to collect before finding the peak
const int numSamples = 3; 

// Variable to store the peak value
int peakValue = 0;

// Variable to store the index of the peak
int peakIndex = 0;

//analogRead bounds for pin 14
int lowerBoundAnalogRead_14 = 94;
int upperBoundAnalogRead_14 = 950;

//voltage bounds for pin 14
int lowerBoundVoltage_14 = 300;
int upperBoundVoltage_14 = 3000;

//analogRead bounds for pin 15
int lowerBoundAnalogRead_15 = 170;
int upperBoundAnalogRead_15 = 1023;

//voltage bounds for pin 15
int lowerBoundVoltage_15 = 10;
int upperBoundVoltage_15 = 3300;

void setup() {
  Serial.begin(9600);  // Initialize the serial communication
  pinMode(pos_Vout, INPUT);
  pinMode(neg_Vout, INPUT);
}

void loop() {
  //Uncomment the next three lines for bound calibration
  //Serial.println(pos_Vout);
  //Serial.println(neg_Vout);
  //delay(5);

  
  long SumSensor = 0;  // Variable to store the sum of the samples
  long sumforceReading = 0;

  // Read and sum the analog samples
  for (int i = 0; i < numSamples; i++) {
    float SumSensor_upper = map(analogRead(pos_Vout), lowerBoundAnalogRead_14, upperBoundAnalogRead_14, lowerBoundVoltage_14, upperBoundAnalogRead_14); 
    float SumSensor_lower = map(analogRead(neg_Vout), lowerBoundAnalogRead_15, upperBoundAnalogRead_15, lowerBoundVoltage_15, upperBoundVoltage_15);
    float difference = SumSensor_upper - SumSensor_lower;
    sumforceReading += difference;
  }

  // Calculate the average
  float average = (float)sumforceReading / numSamples;

  //print to the serial monitor for python to csv converter
  Serial.print(average);

}

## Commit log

2025-03-09 Add ipynbs for aligning and curve fitting for FT and FSR data
    [FSR_test_data.csv, FT_test_data.csv]
2025-03-18 Add script for comparing ground-truth and predicted force
    [FSR_test_data.csv, FT_test_data.csv, vers_1_aligned.csv]
2025-04-03 Added Data folder
    [FSR_flat_2mm_s1.csv, FSR_flat_2mm_s1_exp.csv, FSR_flat_2mm_s2.csv, FSR_flat_2mm_s2_exp.csv]
2025-04-03 Updated Read_FSRs.py
    [FSR_with_temp.csv]
2025-04-15 Add calibration fit using shallow MLP in calibration_models.py
    - Changed so preprocessing no longer scales and retains originals scales
2025-04-17 Changes to calibration_models.py and apply to flat data
    - Allow to choose between first peak vs absolute peak detected
    - Convert timestamps to same time scale (i.e. microseconds to seconds)
2025-12-16 Final Arduino data collection code
    Supports data collection of up to 16 FSRs and 1 thermistor
2025-12-16 Box for PCB version
    CAD .3mf files for electrical box for version 2 of the sensor which uses a PCB for circuitry
    [Instrumented Feeding Bottle Box v3 v3.3mf]
2025-12-16 Rename Instrumented Feeding Bottle Box v3 v3.3mf to Instrumented Feeding Bottle Box v2.3mf
    [Instrumented Feeding Bottle Box v2.3mf]
2025-12-16 Added PCB Gerber Files
    v2 PCB Gerber files used to order boards
2025-12-16 Rename Board Schematic.SchDoc to Altium/Board Schematic.SchDoc
    [Board Schematic.SchDoc]
